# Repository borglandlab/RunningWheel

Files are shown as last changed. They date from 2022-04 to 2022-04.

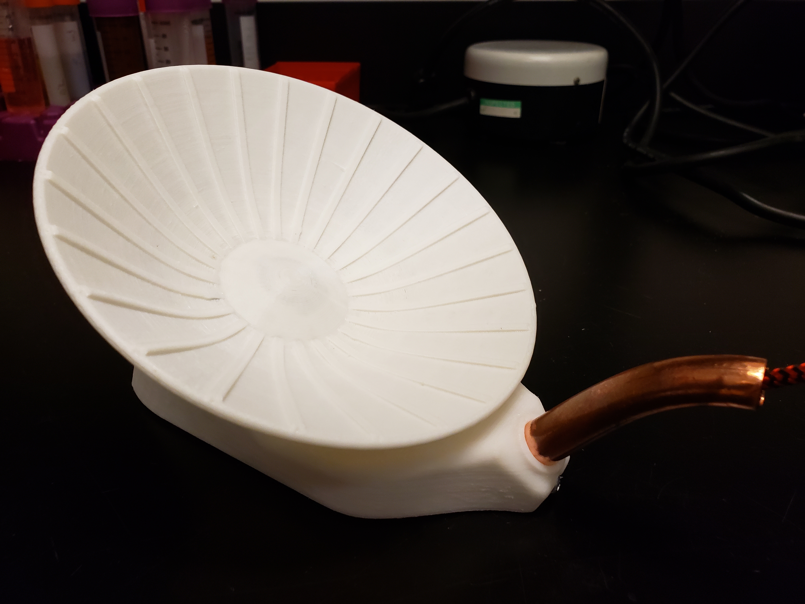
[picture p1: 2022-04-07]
Pictures/RunningWheel_complete.jpg

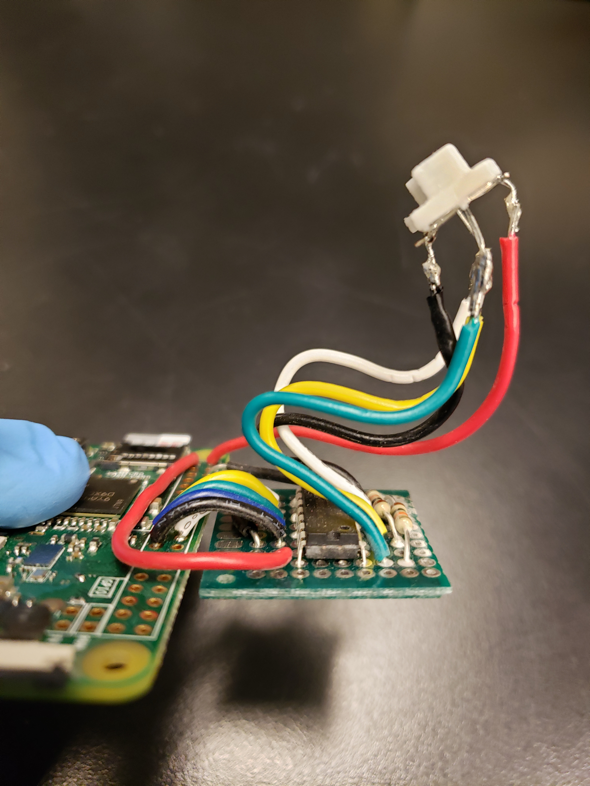
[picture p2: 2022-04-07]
Pictures/RPi_side.jpg

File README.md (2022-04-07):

# Open Source Running Wheel for the Activity-Based Anorexia Model
Nathan Godfrey, Kehan Chen, Temoor Tayyab, and Stephanie Borgland

------
## Brief Description
We designed and constructed an open source [running wheel system](https://github.com/borglandlab/RunningWheel/blob/main/Schematics/Wheel_Schematic.jpg) that runs independent of a central computer. The body of these wheels are 3D printed. The wheels operate using a raspberry pi zero W, a small but highly available microprocessor, and are programmed completely in python. Data is transmitted to a personal computer, that can be located anywhere, via email, where it is then automatically downloaded, parsed, and analyzed with python and MATLAB programs. Our running wheel system is simple, adaptable, and completely open source. 

------
## Cost of Running Wheel
| Item									| Supplier				| Unit Cost	| Needed	| Total Cost |
| -------								| ------				| ------	| -----		| -----	     |
| Raspberry Pi Zero W with 16 GB MicroSD card				| BuyaPi.ca				| $34.33	| 1		| $34.33     |
| 10 BIT, 200KSPS, DIP-16 Analog to Digital Converter (MCP3008-I/P)	| Newark Element14			| $3.60		| 1		| $3.60	     |
| PCB Breakout Board	  	    	    	      			| Amazon 				| $1.27		| 1		| $1.27	     |
| Bestol A1302 Ratiometric Linear Hall Effect Sensor Chip		| Amazon				| $1.90		| 3		| $5.70	     |
| 10Kohm resistors	   	       	      	     			| B & E Electronics LTD (Calgary)	| $0.15		| 3		| $0.45	     |
| USB power cable							| Amazon	    			| $4.33		| 1		| $4.33	     |
| USB wall power adapter						| Amazon				| $4.60		| 1		| $4.60	     |
| TUOFENG 20 Gauge Solid Wire						| Amazon				| $0.93		| 1		| $0.93	     |
| 4x2 mm circular magents						| Amazon				| $0.08		| 12		| $0.96	     |
| 8/8 X 7/8 X 9/32 Rubber Seal Ball Bearing				| PM Hobbycraft (Calgary)		| $2.10		| 1		| $2.10	     |
| #4 x 3/8-inch wood screws    	    					| Home Hardware (Calgary)		| $0.16		| 2		| $0.32	     |
| Protective 1/2" copper tubing						| Rona (Calgary)			| $1.11		| 1		| $1.11	     |
| Base Bottom (~22 g of PLA)	  	 				| $29.99/kg from Amazon			| $0.66		| 1		| $0.66	     |
| Base Top (~60 g of PLA)						| $29.99/kg from Amazon			| $1.80		| 1		| $1.80	     |
| Spinner (~72 g of PLA)						| $29.99/kg from Amazon			| $2.16		| 1		| $2.16	     |
| Sensor Holder (~1 g of PLA)						| $29.99/kg from Amazon			| $0.03		| 1		| $0.03	     |
| **Total Cost**								| 					| 		| 		| **$64.35**   |

-----
## Printing and Assembly

### 3D Printing
There are four pieces that need to be printed for each running wheel. It is best to print all pieces for a single wheel from the same printer, as this will improve how well the parts will fit together. The pieces included:
1. [Base Bottom](https://github.com/borglandlab/RunningWheel/blob/main/3Dprintingfiles/STL/Base%20Bottom.STL)
2. [Base Top](https://github.com/borglandlab/RunningWheel/blob/main/3Dprintingfiles/STL/Base%20Top.STL)
3. [Sensor Holder](https://github.com/borglandlab/RunningWheel/blob/main/3Dprintingfiles/STL/Sensor%20Holder.STL)
4. [Spinner](https://github.com/borglandlab/RunningWheel/blob/main/3Dprintingfiles/STL/Spinner.STL)

It is ideal to print the Spinner part with the same infill settings across all running wheels, as this will decrease the variability in weight. Spinners with different weights will spin differently, changing the experience of the mouse and the likelihood that they will use the wheel.

To facilitate greater reproducibility of our 3D printed running wheels, we’ve outlined printer specifications that we selected, and a summary of the printing process.

Following printing of the Spinner magnets must be inserted into the three rectangular openings left. 3 to 4 4x2 mm circular magnets should fit snuggly. Make sure the same number of magnets is in each opening so that the weight is even. The metal ball bearing should also be inserted into the centre opening. The Spinner is designed to hold a 8/8 X 7/8 X 9/32 ball bearing.

Following printing of the Base Top the support material can be removed. A layer of epoxy glue should also be added to the protrusion that the spinner slides onto. This can be done with a medium size paint brush. After the epoxy has hardened (approximately 24 to 48 hours), it should be carefully sanded down until the ball bearing inside of the Spinner can slide on snuggly. If you sand too much away then reapply the epoxy and try again. This makes the protrusion much stronger so that it won’t wear away with the sliding.

#### Specifications for the eryone thinker ER20 and flsun qqs-pro printers
- Adhesion Type: Skirt
- Alternate Extra Wall: Yes
- Avoid Printed Parts When Traveling: Yes
- Combing mode: All
- Custom support blocker for “[Base Top.stl](https://github.com/borglandlab/RunningWheel/blob/main/3Dprintingfiles/STL/Base%20Top.STL)”: Only print support material where the slanted roof section meets the horizontal roof section. Place support blockers covering the rest of the Base Top. See [attached images](https://github.com/borglandlab/RunningWheel/tree/main/3Dprintingfiles/SupportBlockers) to see where to place the support material.
- Enable Retraction: Yes
- Extrude width: 0.46 mm (wall/top/bottom/infill/everything)
- Infill Line Distance: 6.9 mm
- Infill Density: 7%
- Infill Overlap Percentage: 25%
- Infill Patter: Zig zag
- Infill Travel Optimisation: Yes
- Initial Layer Height: 0.24 mm
- Layer height: 0.2 mm
- Material: Generic PLA
- Optimizing wall printing order: Yes
- Print Cooling: 70% at all times
- Print Temperature: 200C (nozzle), 40C (bed)
- Speed: 50 mm/s everything
- Initial Speed: 30 mm/s
- Wall Line count: 2

Before mass printing, the printer bed was cleaned with isopropyl alcohol. An outline of the part was then printed, followed by light glue stick application to the area. After each print, the old purge line/skirt was scraped off the bed. Before printing again, the area was cleaned with a lightly dampened cloth and the print area was again prepared with light glue stick application.

#### Specifications for the Sindoh 3DWOX
- Advanced mode on
- Basic Settings:
- Layer height: 0.2 mm
- Nozzle Temperature: 200C
- Bed Temperature: 40C
- Infill Density: 7%
- Flow Compensation: 100%
- Quality/Shell Settings:
- Bottom Layer Thickness: 0 mm
- Bottom Layer Line Width: 200%
- Retraction Combing: All
- Internal Moving Area: Default
- Wall Thickness: 0.88 mm
- Top/Bottom Thickness: 0.80 mm
- Solid Top: yes
- Solid Bottom: yes
- Wall Printing Direction: Inside to Outside
- Infill Settings:
- Infill Patter: Automatic
- Infill Overlap: 25%
- Skin Type: Line
- Skin Overlap: 15%
- Speed Settings:
- Print Speed: 50 mm/s
- Travel Speed: 130 mm/s
- First Layer Speed: 30 mm/s
- Infill Speed: 0 mm/s
- Top/Bottom Speed: 0 mm/s
- Outer Wall Speed: 0 mm/s
- Inner Wall Speed: 0 mm/s
- Retraction/Cooling Settings:
- Enable Retraction: yes
- Speed: 30 mm/s
- Length: 6.00 mm
- Minimal Travel: 1.50 mm
- Minimal Extrusion Before Retraction: 0.02 mm
- Lowering Bed during Retraction: 0 mm
- Regular Fan Speed: 50%
- Maximum Fan Speed: 50%
- Height at Regular Fan Speed: 0.60 mm
- Enable Cooling Fan: yes
- Minimal Layer Time: 5 sec
- Minimum Speed: 10 mm/s
- Minimum wait period for Lowering Bed: no
- Support:
   - Support: none
   - Bed Adhesion:
   - Bed Adhesion: skirt
   - Skirt Line Count: 1
   - Skirt Line Gap: 3 mm
   - Skirt Minimal Length: 150 mm
- Shape Error Correction: 
   - Combination Mode A: yes

With these settings, the printer will print no support blockers. However, for “[Base Top.stl](https://github.com/borglandlab/RunningWheel/blob/main/3Dprintingfiles/STL/Base%20Top.STL)” support material should be printed where the slanted roof section meets the horizontal roof section. You need to manually add this. See [attached images](https://github.com/borglandlab/RunningWheel/tree/main/3Dprintingfiles/SupportBlockers) to see where to place the support material.

### Assembling the Running Wheel
Each wheel must be assembled using the following electrical components and wiring information. A soldering iron and solder are required to do this.

The 3 hall effect sensors must be inserted inside the 3D printed sensor holder prior to being soldered. This sensor holder fits nicely in the base top of the running wheel.

Electrical Components:
- Raspberry Pi 0 W with a microSD card:
- The MCP 3008 analog to digital converter (ADC)
- 3 A1302 continuous time ratiometric linear hall effect sensors
- 3 10kohm resistors
- A 10 x 10 PCB breakout board (this can be cut to size)
- 20 gauge solid core wires

Wiring (follow the [electrical schematic](https://github.com/borglandlab/RunningWheel/blob/main/Schematics/Electrical_Schematic.jpg)):
- The MCP3008 ADC is soldered to the 10 x 10 PCB breakout board
- Pin 16 (VDD) and pin 15 (Vref) of the MCP3008 are both connected to pin 1 (3.3 V) of the Raspberry Pi.
- Pin 14 (Agnd) and Pin 9 (Dgnd) of the MCP3008 are both connected to pin 6 (ground) of the Raspberry Pi.
- Pin 13 (CLK) of the MCP3008 is connected to pin 23 (GPIO 11) of the raspberry pi.
- Pin 12 (Dout) of the MCP3008 is connected to pin 21 (GPIO 9) of the raspberry pi.
- Pin 11 (Din) of the MCP3008 is connected to pin 19 (GPIO 10) of the raspberry pi.
- Pin 10 (CS/SCDN) of the MCP3008 is connected to pin 24 (GPIO 8) of the raspberry pi.
- Pin 1 of the left (hf1), centre (hf2), and right (hf3) hall effect sensors are all connected to pin 2 (5 V) of the raspberry pi.
- Pin 2 of the left (hf1), centre (hf2), and right (hf3) hall effect sensors are all connected to pin 6 (ground) of the raspberry pi.
- Pin 3 of the left (hf1) hall effect sensor is connected to pin 5 (CH4) of the MCP3008.
- Pin 3 of the centre (hf2) hall effect sensor is connected to pin 3 (CH2) of the MCP3008.
- Pin 3 of the right (hf3) hall effect sensor is connected to pin 1 (CH0) of the MCP3008.
- Each hall effect sensor has a pull-down resistor connecting pin 3 to ground.

For your reference, we've included images of the electrical assembly from the [back](https://github.com/borglandlab/RunningWheel/blob/main/Pictures/RPi_behind.jpg), [front](https://github.com/borglandlab/RunningWheel/blob/main/Pictures/RPi_above.jpg), and [side](https://github.com/borglandlab/RunningWheel/blob/main/Pictures/RPi_side.jpg).

-----
## Raspberry Pi Zero W Set up
There are two ways to set up the software on your raspberry pi zero for running wheel use.
1. Clone an SD card
2. Manually install operating system, 3rd party modules, and spinner.py file

### 1. Clone an SD card
On my mac I used an app called [ApplePiBaker](https://www.tweaking4all.com/software/macosx-software/applepi-baker-v2/) to clone an SD card and copy it to a new SD card. You can find the documentation for the ApplePiBaker online.

### 2. Manual installation

#### Downloading Operating System
1. Install [Raspberry Pi Imager](https://www.raspberrypi.com/software/) on your personal computer (This is available for Windows, macOS, and Linux)
2. Insert an SD card into your computer
3. Format the SD card
4. Use Raspberry Pi Imager to load the Raspberry Pi operating system onto the SD card:
   - Operating System: RASPBERRY PI OS (32-BIT)
   - Storage: selected empty SD card
   - Click “Write”

#### Setting up Raspberry Pi
1. Put SD card into Raspberry Pi and turn on - will reboot
2. Set up Country, Language, and Timezone according to your actual timezone
   1. Will ask you to change password. We’ve left ours without a password
3. Select internet connection you plan to use and input password
   1. We’ve connected to our University’s guest account. To ensure that we don’t get kicked out everytime, we’ve added the MAC address for each RPi to the network so that they are permanently in the system. We did this through the IT department.
      1. To find the MAC address, open Terminal and enter “ifconfig” and follow the instructions found at this [website](https://raspberrytips.com/mac-address-on-raspberry-pi/)
      > The MAC address just after the keyword “ether” in the section corresponding to your network interface. It's represented as a 12-digit hexadecimal number (AA:BB:CC:DD:EE:FF).
4. Allow for system to update - this can take a while
5. Reboot/Restart RPi

#### Install Adafruit libraries and configure pi for SPI interface
1. Make sure the Raspberry Pi is connected to the internet
2. Open Terminal
3. Enter: “sudo pip3 install adafruit-blinka”
4. Enter: “sudo pip3 install adafruit-circuitpython-mcp3xxx”
5. Enter: “sudo raspi-config” --> 3 Interface Options —> P4 SPI —> Would you like the SPI interface to be enabled? - “Yes”
6. Enter “sudo reboot”
```{console}
pi@raspberrypi:~ $ sudo pip3 install adafruit-blinka
pi@raspberrypi:~ $ sudo pip3 install adafruit-circuitpython-mcp3xxx
pi@raspberrypi:~ $ sudo raspi-config
# 3 Interface Options —> P4 SPI —> Would you like the SPI interface to be enabled? -> “Yes”
pi@raspberrypi:~ $ sudo reboot
```

#### Install third party module
1. Install Speedtest
```{console}
pi@raspberrypi:~ $ sudo pip3 install speedtest-cli
pi@raspberrypi:~ $ sudo reboot
```

#### Copying python code to RPi
1. Insert USB drive into RPi containing [python code for spinner](https://github.com/borglandlab/RunningWheel/blob/main/Spinner_Code/spinner_WIFI.py)
2. Change name of file from spinner_WIFI.py to spinner.py
3. Copy spinner.py file to RPi from USB drive
4. Change number in text editor to correspond with spinner number ('SPINNER_NAME')
   1. This must be different for each spinner and must be a whole number
6. Update email address ('GMAIL_USERNAME')
7. Update email address password ('GMAIL_PASSWORD')
8. This is also where you you can adjust how often the wheels will send an email ('EMAIL_FREQUENCY') and how easily the hall-effect sensors will trigger ('TRIGGER_THRESHOLD')

```{python}
SPINNER_NAME = 1  #Corresponds to the wheel number
EMAIL_FREQUENCY = 1     #Corresponds to how often an email will be sent, once every _____ hour.
TRIGGER_THRESHOLD = 30
#Email Variables
SMTP_SERVER = 'smtp.gmail.com' #Email Server (don't change!)
SMTP_PORT = 587 #Server Port (don't change!)
GMAIL_USERNAME = 'email@gmail.com' #change this to match your gmail account
GMAIL_PASSWORD = 'password'  #change this to match your gmail password
```

#### Setting up RPi for python program to automatically run at start-up/reboot
1. Open Terminal
2. Enter: “sudo crontab -e”
   1. Crontab is included in Raspbian
3. Scroll to the very bottom and enter: “@reboot sleep 60 && sudo python3 /home/pi/Desktop/spinner.py”
4. Control x --> “Y” --> Enter
5. cd to directory of your script. In our case it’s desktop so we will enter: “cd /home/pi/Desktop/”
6. Chmod file to make it executable by the computer; enter: “sudo chmod +x spinner.py”
7. Reboot, enter: “sudo reboot”
   1. Every time you change the .py file you need to run the chmod
   2. Is also useful as a test
```{console}
pi@raspberrypi:~ $ sudo crontab -e
# scroll to bottom and enter "@reboot sleep 60 && sudo python3 /home/pi/Desktop/spinner.py”
pi@raspberrypi:~ $ cd /home/pi/Desktop/
pi@raspberrypi:~/home/pi/Desktop $ sudo chmod +x spinner.py
pi@raspberrypi:~/home/pi/Desktop $ sudo reboot
```

#### Notes
1. I’ve found that deleting the text file before running new experiments keeps things from corrupting and not working properly.

#### Cloning
Once the raspberry pi is setup, you can clone the SD card as a backup.zip file. Then just clone the backup onto all of your SD cards. After doing this, you will need to go on your raspberry pi to change the name of the spinner on the spinner.py file. Then do the following:
1. Open Terminal
2. cd to directory of your script. In our case it’s desktop so we will enter: “cd /home/pi/Desktop/”
3. Chmod file to make it executable by the computer; enter: “sudo chmod +x spinner.py”
4. Reboot, enter: “sudo reboot”
```{console}
pi@raspberrypi:~ $ /home/pi/Desktop/
pi@raspberrypi:~/home/pi/Desktop $ sudo chmod +x spinner.py
pi@raspberrypi:~/home/pi/Desktop $ sudo reboot
```
This is faster and easier than setting them all up individually.
However, you will still need to make sure that you have the MAC addresses for each raspberry pi.

-----
## Running Wheels with no wifi connection

If you are running your experiments with no, or a very weak/unreliable wifi connection, then you may wish to use the no wifi mode. To run the no wifi mode, these changes from the previous instructions will need to be made:
1. You do not need to install the third party module, Speedtest.
2. You do not need to connect to the wifi during setup.
3. Copy the [no wifi spinner code](https://github.com/borglandlab/RunningWheel/blob/main/Spinner_Code/spinner_noWIFI.py) to the raspberry pi instead of the wifi version.
4. Change name of file from spinner_noWIFI.py to spinner.py
5. Copy spinner.py file to RPi from USB drive
6. Change number in text editor to correspond with spinner number ('SPINNER_NAME')
   1. This must be different for each spinner and must be a whole number
8. This is also where you you can adjust how often the wheels will send an email ('EMAIL_FREQUENCY') and how easily the hall-effect sensors will trigger ('TRIGGER_THRESHOLD')

```{python}
SPINNER_NAME = 1  #Corresponds to the wheel number
TRIGGER_THRESHOLD = 30
```

-----
## Setting up the Running Wheels

To supply power to the raspberry pi a micro USB cable must be connected to the outside micro USB port. The inner micro USB port can only transmit data, so you can plug your keyboard and stuff into that one when you need to. There is also a micro HDMI port that can be used when to connect a monitor. This is on the opposite side from the micro USB power port. You will most likely need a micro HDMI adapter to use this.

Before running connect each raspberry pi to a power source, keyboard (with joystick and trackpad), and monitor. Allow the raspberry pi to boot up. Once the desktop is open, remove or delete the text file. This will ensure that the new data collected in the text file will only be from the current experiment. Unplug the raspberry pi.

When setting up the running wheels, carefully insert the raspberry pi into the Base Top so that the senor holder with sensors is lined up with the hold in the base top. This may require some careful bending of the wires connected to the sensors. The raspberry pi should fit into notches printed on the base bottom. Connect the raspberry pi to a micro USB power cable that is not yet connected to a power supply. Put the screws in place in the front and back of the base top to keep the base bottom connected. Slide the Spinner with the ball bearing on the protrusion of the base top. The running wheel is now ready for calibration. Depending on how much light your 3D printed running wheel base lets through, you may also wish to cover the ACT LED on the raspberry pi with opaque tape.

It is important to note that the mice will chew the USB power cable. We’ve tried a number of different things, but the only reliable solution is to cut and bend copper tubing to protect the cable. The hole in the front of the base top is designed to snuggly fit ½” copper tubing. Tube bending springs can be used to change the shape of the copper tubing without causing kinks. However, you will need to avoid really tight bends because the micro USB cable still needs to be able to slide through the tubing. This will require some playing around to get right depending on how you are setting the wheels up and what type of cage you are using.

We've included a image of a [completely assembled running wheel](https://github.com/borglandlab/RunningWheel/blob/main/Pictures/RunningWheel_complete.jpg) for your reference.

### Calibration

Each running wheel is automatically calibrated at start-up. Each time the wheels are connected to power, the spinner must be taped so that the magnets are as far away from the sensors as possible. There are three circular notches on the top of each spinner to aide in identifying the location of the magnets. Prior to connecting to power, running wheels should be placed in the cage in the environment where the experiment will take place. The calibration cycle will begin immediately after the running wheel is connected to power and takes about two to three minutes. You will be notified that the calibration cycle is complete by an email. Remove tape and place mouse in cage. If you are using the no wifi spinner.py version then assume that the calibration has been completed after 3 minutes have passed.

Triggering of the hall-effect sensors will occur when read values are more than 30 above or below the maximum and minimum values read during the calibration cycle. Calibration only needs to be done once at the beginning of the experiment, or after any time the running wheel is disconnected from its power supply.

It is important to bear in mind that hall-effect sensors detect changes in the magnetic field. Hence, any large fluctuations in the magnetic field other than the movement of the magnets on the bottom of the spinner will result in experimental noise. For this reason, it is important to ensure that the environment where you are running these experiments does not have large fluctuations in the magnetic field. Even in a good environment, some magnetic noise will most likely be detected, but it should be infrequent enough so that it will not noticeably change results.

If you feel that there is too much noise, there are a few different solutions:
1.	Disconnect and reconnect the wheel to the power supply to allow for the calibration sequency to run again. It is possible that the baseline noise has changed since calibration was initially done.
2.	Change power supply. It’s possible that the power supply that you are using is noisy.
3.	Change rooms. This may not be an option, but a room with less electrical noise is ideal.
4.	Increase the threshold on the spinner.py. The default threshold value is 30, but this could be increased to 40 or 50. We have only tested the wheels with a threshold value of 30, so we recommend you run some tests to ensure that your higher threshold will still be triggered by the magnets.
5.	Resolder the connections of electrical components.

-----
## Software for using Running Wheel

I have created software for both [macOS](https://github.com/borglandlab/RunningWheel/blob/main/WheelAnalysis_macOS.md) and [Windows](https://github.com/borglandlab/RunningWheel/blob/main/WheelAnalsis_Windows.md). Click on the appropriate link to be taken to the setup and use instructions.

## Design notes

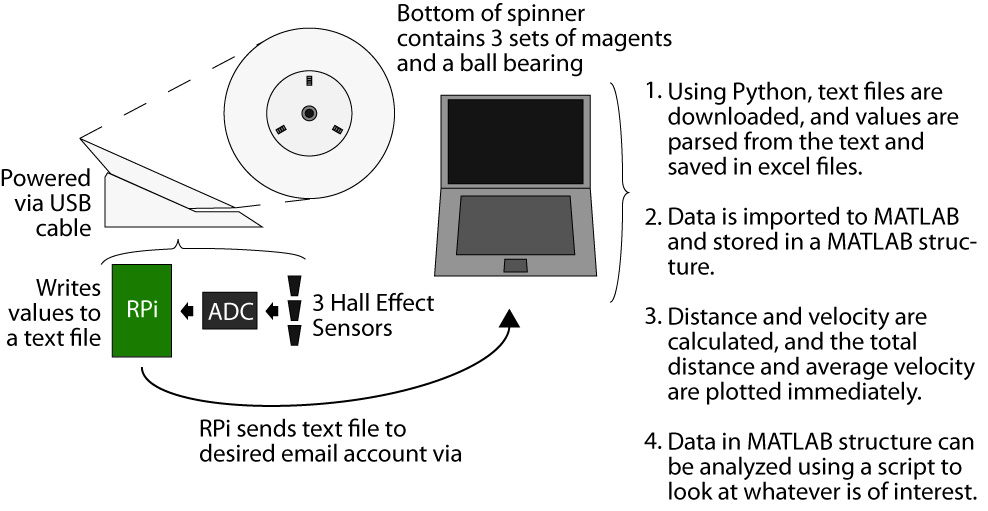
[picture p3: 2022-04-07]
Schematics/Wheel_Schematic.jpg

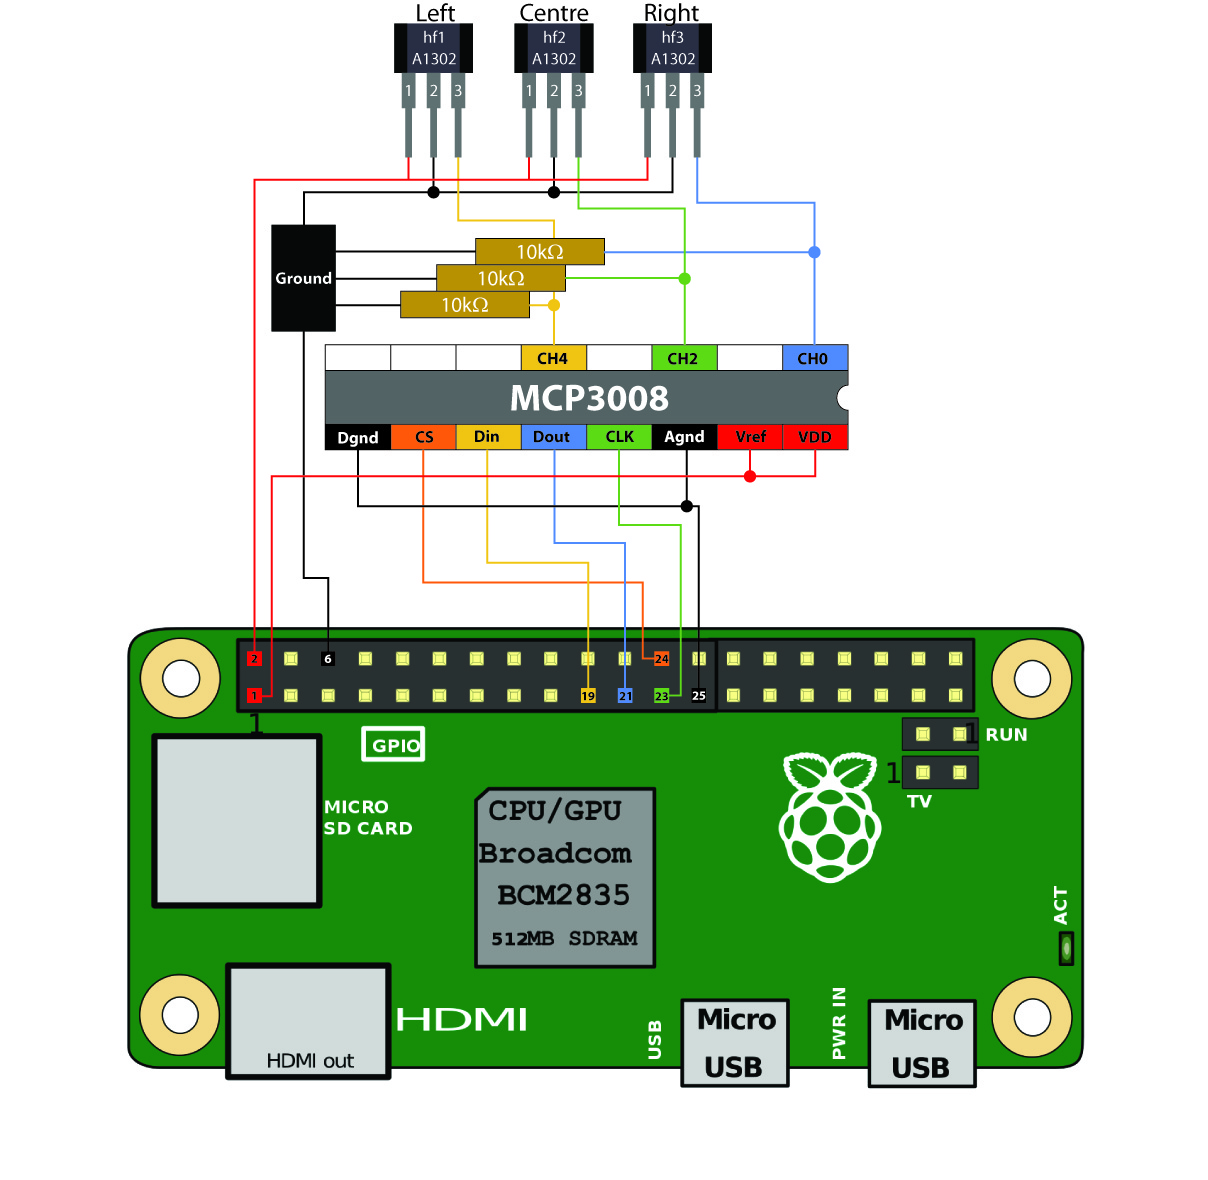
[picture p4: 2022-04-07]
Schematics/Electrical_Schematic.jpg

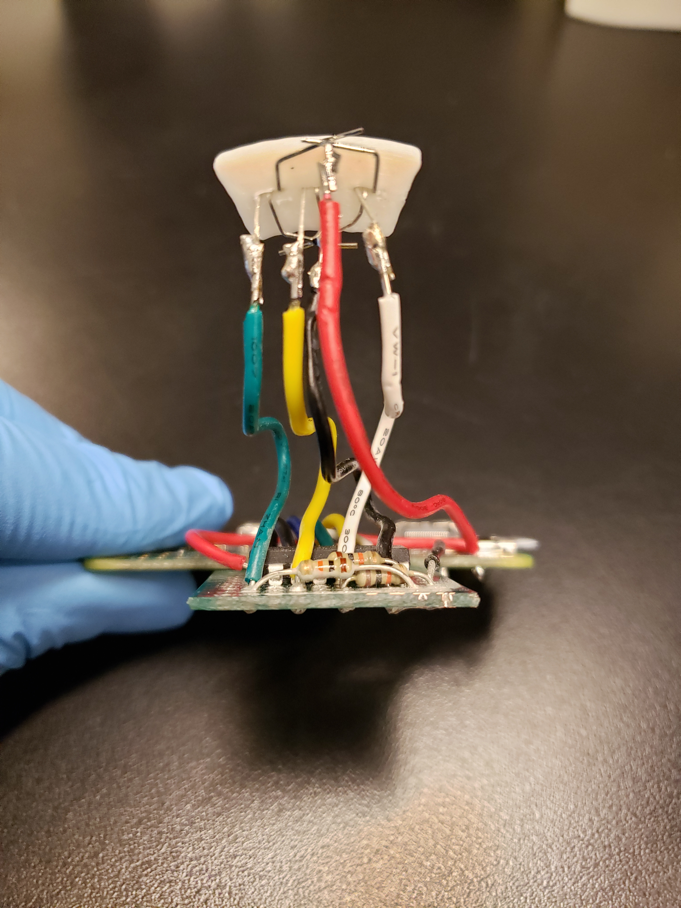
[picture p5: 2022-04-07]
Pictures/RPi_behind.jpg

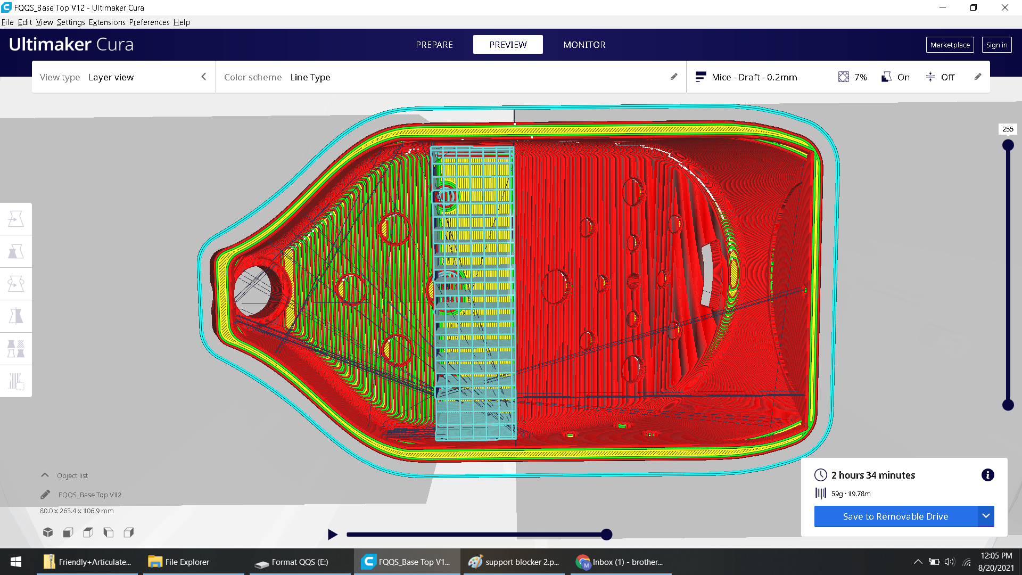
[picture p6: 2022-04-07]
3Dprintingfiles/SupportBlockers/support blocker 3.png

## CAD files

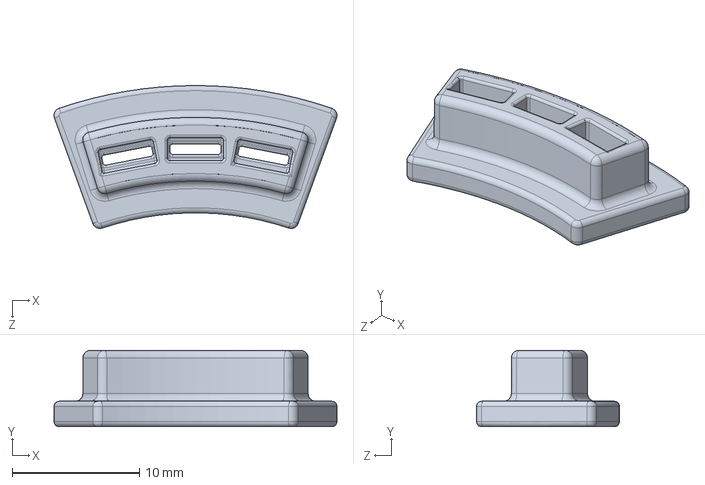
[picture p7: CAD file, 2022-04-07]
3Dprintingfiles/SLDPRT/Sensor Holder.SLDPRT
22.2 x 6.00 x 11.2 mm

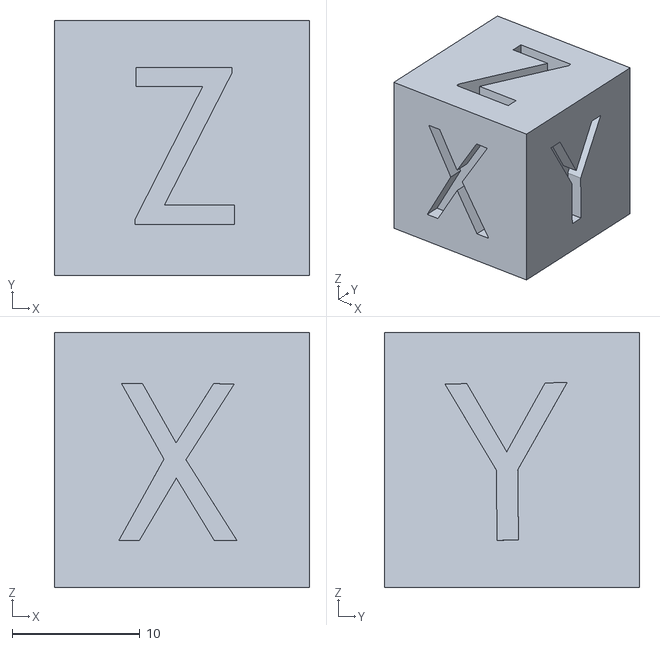
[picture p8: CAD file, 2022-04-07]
3Dprintingfiles/STL/xyzCalibration_cube.stl
20.0 x 20.0 x 20.0

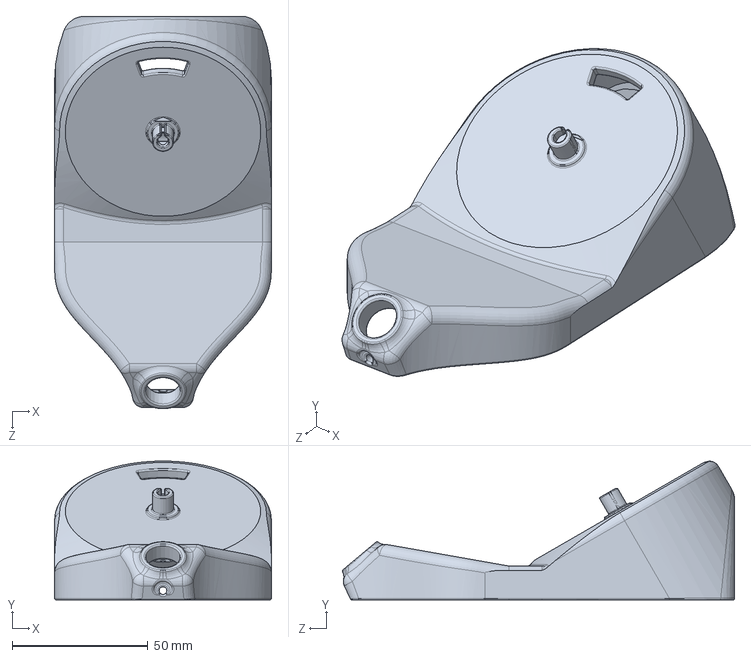
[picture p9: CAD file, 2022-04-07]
3Dprintingfiles/SLDPRT/Base Top.SLDPRT
80.0 x 51.2 x 144.7 mm

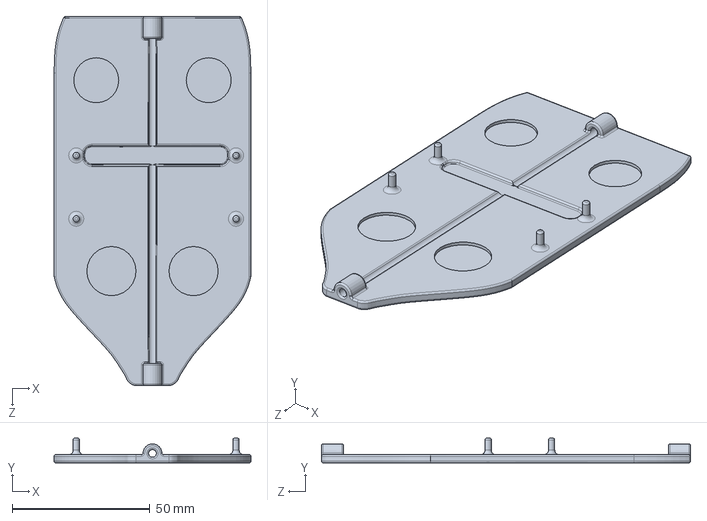
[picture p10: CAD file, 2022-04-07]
3Dprintingfiles/SLDPRT/Base Bottom.SLDPRT
71.4 x 9.00 x 133.9 mm

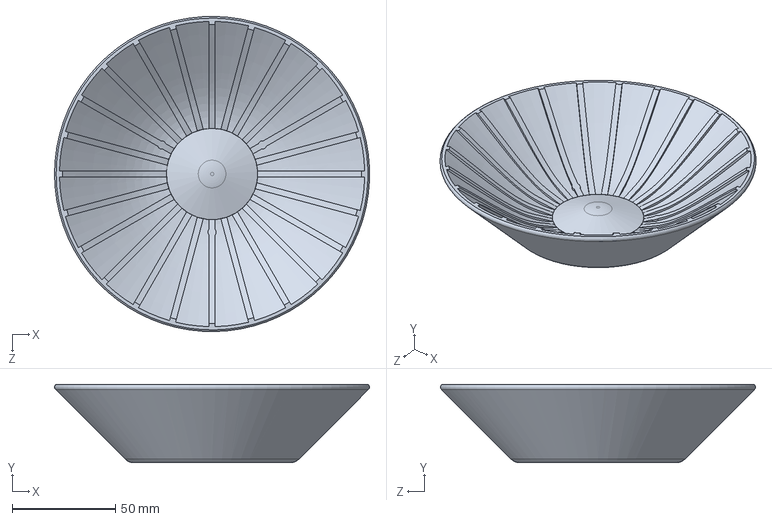
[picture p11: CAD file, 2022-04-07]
3Dprintingfiles/SLDPRT/Spinner.SLDPRT
152.6 x 38.0 x 152.6 mm

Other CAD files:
3Dprintingfiles/STL/Base Bottom.STL
3Dprintingfiles/STL/Base Top.STL
3Dprintingfiles/STL/Sensor Holder.STL
3Dprintingfiles/STL/Spinner.STL

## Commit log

2022-04-07 Update README.md
    added description at the beginning and links to wheel and electrical schematics, and added links to apple pi baker and raspberry pi imager
2022-04-07 Uploaded the 3D printed files
    3D printed files and images of the support blockers.
    [Base Bottom.SLDPRT, Base Bottom.STL, Base Top.SLDPRT, Base Top.STL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]
2022-04-07 Added links to 3D printing files
2022-04-07 Add Analysis Code
    [ABA.xlsx]
2022-04-07 Add Speedtest installation
    Added Speedtest installation to raspberry pi
2022-04-07 Cut code analysis
    I moved the code analysis to a different readme. I will have one for mac and one for windows.
2022-04-07 Add setup and calibration
